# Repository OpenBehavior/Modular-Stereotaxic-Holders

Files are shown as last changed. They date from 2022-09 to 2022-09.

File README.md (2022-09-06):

# Modular-Stereotaxic-Holders
modular stereotaxic holder for implanting optic fibers, guide cannulas, and GRIN anchors

Designed by Andrew Hardaway (andrewhardaway@uabmc.edu)

This is a collection of 3D print designs for making stereotaxic arms that can be used to place optic fibers, guide cannulas, and GRIN anchors.

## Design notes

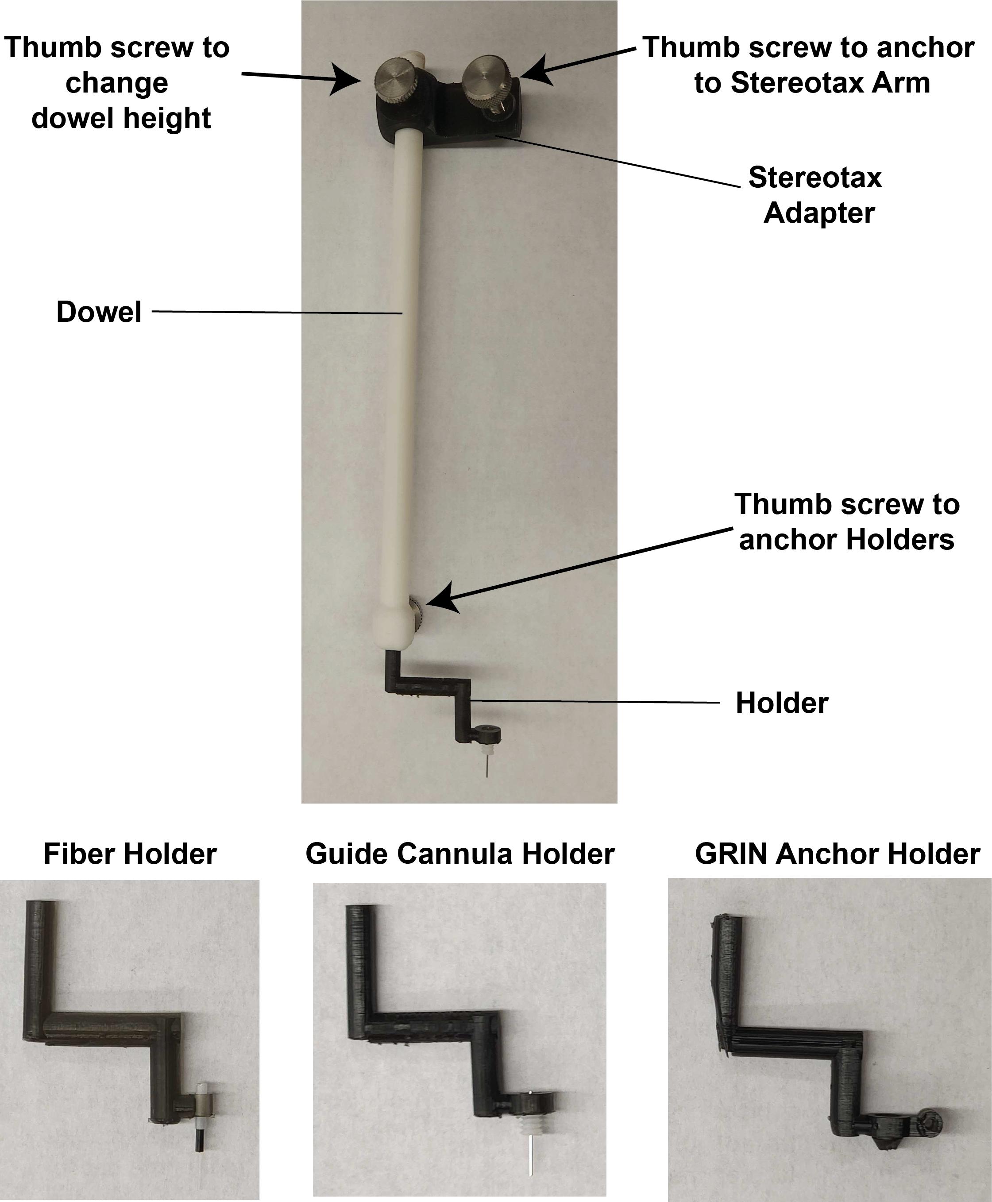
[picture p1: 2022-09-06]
Implant adapters - Andrew Hardaway.png

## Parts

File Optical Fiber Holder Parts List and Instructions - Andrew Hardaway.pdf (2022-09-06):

Assembly of Optical Fiber holders for Stereotaxic Surgery Parts List
Print -
1. Stereotax Arm Adapter
2. Dowel
3. Optical fiber holder
Purchase:
4. Gorilla Glue - 5 min epoxy (https://www.amazon.com/Gorilla-Epoxy-Minute-ounce-Syringe/dp/B001Z3C3AG?th=1)
5. Ceramic Split Sleeves (https://precisionfiberproducts.com/ceramic-split-sleeve/)
6. Stainless Steel Raised Knurled-Head Thumb Screw - 10-32 Thread Size, 3/4" Long, 1/2" Diameter Head (https://www.mcmaster.com/91830A407/)
7. Stainless Steel Raised Knurled-Head Thumb Screw M3 x 0.50 mm Thread Size, 6 mm Long (https://www.mcmaster.com/92558A310/) (2 needed for each holder)
8. uxcell Knurled Threaded Insert, M3 x 3mm (L) x 5mm (OD) Female Thread Brass Embedment Nuts, Pack of 100 (https://www.amazon.com/uxcell-Knurled-Threaded-Insert-Embedment/dp/B07LBGQ2PV)

Instructions after printing:
Heat Sets
For PLA prints, you will need to install the heat sets in three places via a soldering iron and heat set adapter. For resin prints I recommend using gorilla glue epoxy. In either case you want to avoid getting epoxy or excess PLA in the threading of the heat sets. Try to push them in steadily so that they are straight. If you use PLA some excess material might wind up in the cavity of the adapter or dowel end. Use a needle or pliers to fish out this excess while it is still molten from the heat of the soldering iron. If it solidifies it may inhibit use. Do this in two places:
1) the stereotax adapter hole on its front face
2) the end of the dowel
Both heat sets will provide threading for the M3 thumb screws. The thumb screws make removal after the head cap sets SO much easier.
Sleeve attachment
Use epoxy to glue the ceramic split sleeve to the optical fiber holder. Let dry thoroughly before use.
Sanding (Optional but recommended):
Use 400 grit sand paper to sand the non-fiber end of the optical fiber holder that goes into the dowel. This will make it very smooth so that it slides easily in and out of the dowel end. You want a very smooth action so that after release of the thumb screw you can use the z-control of the stereotax arm to pull the dowel off of the optical fiber holder.

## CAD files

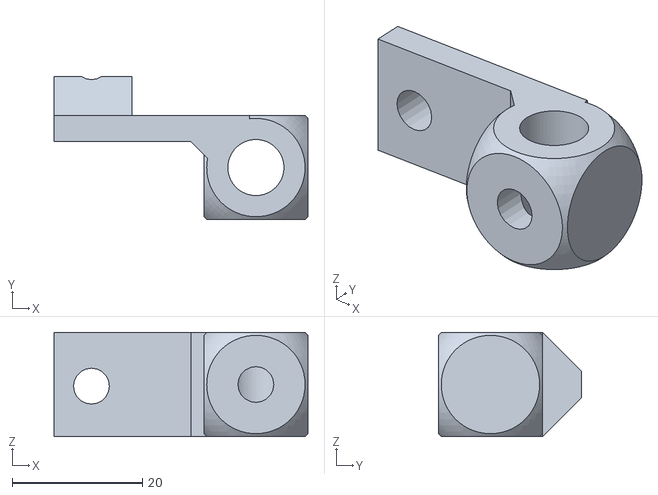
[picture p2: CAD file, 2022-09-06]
Stereotax arm adapter - Andrew Hardaway.stl
39.0 x 22.0 x 16.0

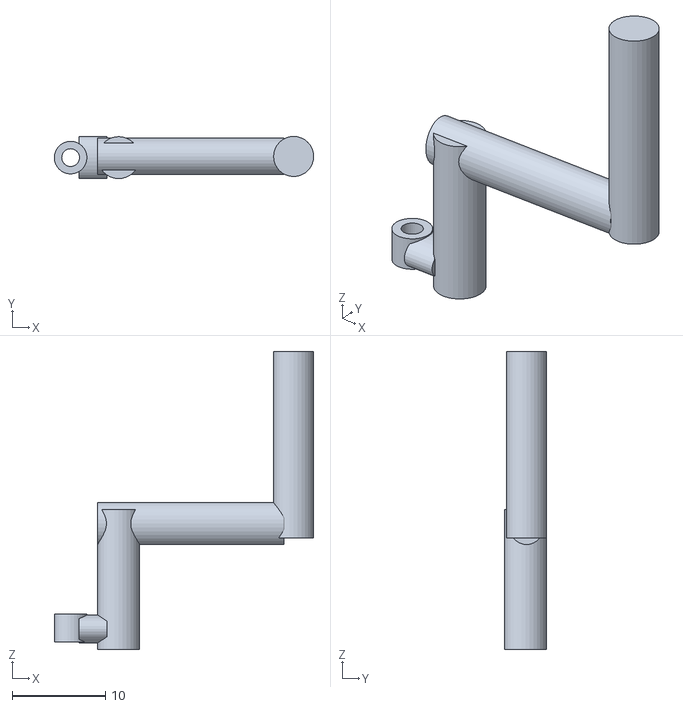
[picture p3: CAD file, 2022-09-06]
Fiber Optic Cannulae holder - Andrew Hardaway.stl
27.8 x 4.53 x 32.0

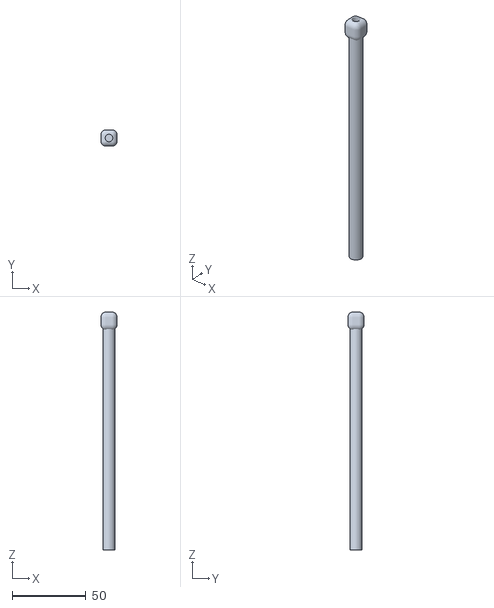
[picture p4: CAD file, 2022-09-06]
Stereotaxic dowel - Andrew Hardaway.stl
11.0 x 11.0 x 161.0

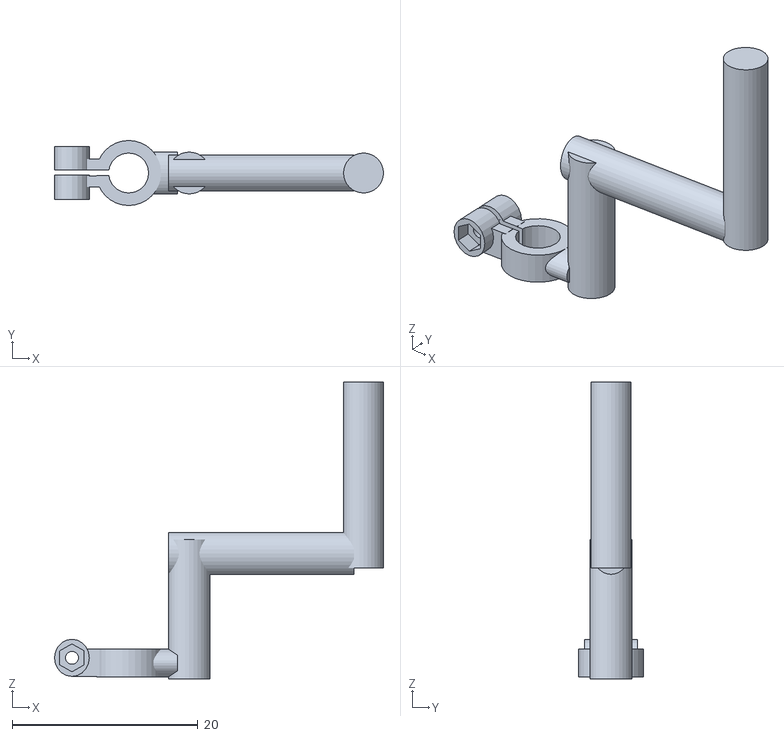
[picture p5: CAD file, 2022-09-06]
GRIN lens anchor disk holder - Andrew Hardaway.stl
35.4 x 7.00 x 31.9

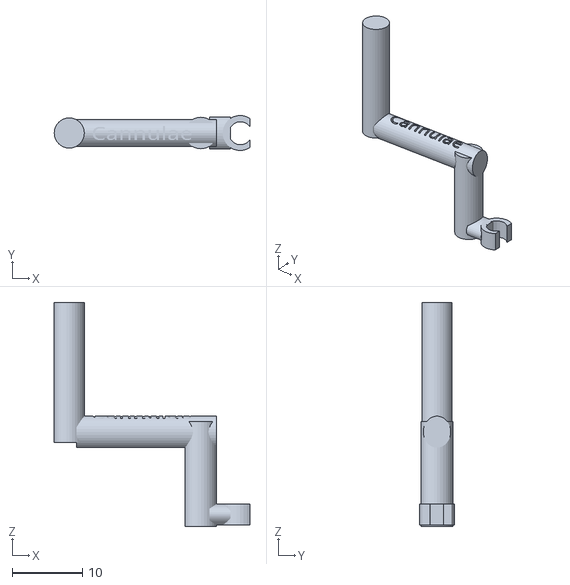
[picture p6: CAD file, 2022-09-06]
Guide Cannulae Holder - Andrew Hardaway.stl
27.9 x 5.00 x 32.0
